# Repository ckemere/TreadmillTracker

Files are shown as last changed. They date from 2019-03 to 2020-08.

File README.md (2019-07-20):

# Raspberry pi based interface for a rodent treadmill

  - MSP430 based HW data acquisition "hat"
  - Rotational angle tracking using the CUI AMT 102/3 quadrature encoders
  - 1 kHz master clock for timestamping 8 IO lines

## Setup overview

### PiHat
The custom Raspberry Pi hat contains several useful features.
- **Eight GPIO pins** can be used for either receiving or sending signals.
- **Encoder data (AMT102)** is received through the six pins at the top of the board.  
- **2 kHz master clock (DSC6083)** reliably timestamps input data.
- **Button** ?
- **MSP430 microcontroller** packages and sends serial messages containing timestamped data every 2 ms. Programmed via seven pins at bottom of board.
- **Shield** interfaces with Raspberry Pi pins, including the eight GPIO pins connected to RaspPi GPIO pins.

### Accessories
#### Rotary encoder
The AMT102 sends signals in increments with resolution of 4096 steps/revolution. Thus each pulse signals that the wheel has turned 1/4096 of a revolution. For more details, look at the specs in the data sheet contained in *Firmware*.

#### Lick sensor
The lick sensor sends digital signals to one of the Hat's GPIO pins to indicate a licking event is occurring. More details in lick-sensor repository.

#### Nose-poke sensor
The nose-poke sensor sends digital signals to one of the Hat's GPIO pins to indicate a nose-poke event is occurring.

#### Syringe pump
The syringe pump receives 5V pulses from a GPIO pin on the Hat to dispense liquid rewards. The duration of the pulse determines the volume of reward dispensed (given a syringe diameter and pump speed).

#### Sound card
The sound card converts the digital audio file (.wav) to an analog signal to drive the external speakers. It can either be integrated with the host computer (if using a desktop), or as a shield (if using a Raspberry Pi; the HiFiBerry Amp2, for example, uses built-in drivers in the Raspberry Pi Linux kernel to obtain high-quality I2C digital audio from the GPIO pins, which it converts to an analog signal for speaker input. See [here](https://www.hifiberry.com/build/documentation/configuring-linux-3-18-x/) for more details.)

#### Breakout board
In order to streamline I/O connections between the custom hat and accessories, a custom breakout board shield connects GPIO pins to the rings of 3.5 mm audio jacks. Additionally, the hat Vdd (3.6 V) can be routed to supply voltage to the tips of the audio jacks. With this setup, audio cables can transmit GPIO signal to input and from output devices listed above. For example, audio cables can carry lick and nose-poke sensor digital signals, or send dispense signals to the syringe pumps.

### Host computer
The host computer can either be a Raspberry Pi or a desktop computer. If using a Raspberry Pi, then the custom hat and sound card shield can be stacked on top of one another to form a three-layer, stand-alone device. Otherwise, the host computer is connected to the custom hat via USB, and the native desktop sound card is used to drive the external speakers. In either case, the following components must be installed on the computer.

#### Mixer
The combination of the JACK Audio Connection Kit and minimixer allows for cross-talk between audio sources to function as a software mixer for different audio signals. The JACK daemon runs in the background as a sound server, built on top of the Advanced Linux Sound Architecture (ALSA), for a particular output device (sound card). In a separate process, the minimixer receives different audio feeds in its virtual channels, and controls each sound level of each channel that it feeds into the JACK daemon based on OSC commands it receives. Thus the user has control to dynamically change the output levels of different virtual channels in the minimixer.

#### OSC interface
The mixer, in turn, is interfaced through an OSC package, such `oscpy` in Python, that binds and sends OSC commands to the same port as the mixer. The commands direct the mixer to increase or decrease the gain for each channel in the mixer.

#### Control script
The control script must manage I/O from all the above components, including:
- Processing **behavior input** from the custom hat to determine the current behavior state. The input messages via the serial interface include current time, wheel encoder position, and GPIO values.
- Controlling **audio output** by launching appropriate audio subprocesses (e.g. daemon, mixer) and sending OSC commands to the mixer based on the current behavior state.
- Controlling **behavior output** by sending dispense pulses to the GPIOs associated with syringe pumps based on the current behavior state.

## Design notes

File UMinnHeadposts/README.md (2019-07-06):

This is a design adapted from that developed by Ghanbari et al and presented in the paper
["Cortex-wide neural interfacing via transparent polymer
skulls"](https://www.nature.com/articles/s41467-019-09488-0) from the lab of Suhasa
Kodandaramaiah at the University of Minnesota. Various curves have been replaced with simpler
splines, mounting holes stretched to 5.5mm, and the 3D printed base and metal frames have been
made to be symmetrical (the 3D printed base at least has a symmetrical hole).

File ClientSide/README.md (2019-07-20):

# Notes on using the Treadmill Tracker

### Using the direct USB interface

#### Set up
Install the udev file in /etc/udev/rules.d directory. This file sets up the proper permissions
for the FT230X interface as well as the latency (see below). Also, add yourself to the proper
groups.

```
sudo cp 60-ftdi-latency.rules /etc/udev/rules.d/
sudo usermod -a -G tty <your-username>
sudo usermod -a -G dialout <your-username>
```

#### Expectations
We are sending 9 byte messages at 256000 baud. Since there is an extra stop byte per serial
transaction, our messages are actually 9 x 9 or 81 bits long, and so our sustained rate can at
most be 256000/81, or more interestingly, our minimum transaction period can be 81/256000 or
0.31 ms. Given that the USB transaction rate is expected to have a period of at least 1 ms, we
suspect the best we can do is 2 ms data transmission rates.

#### Quantifying latency
There's several ways of quantifying latency. 

##### Message rate latency
Since in the absence of any triggered outputs we know the rate that the MSP430 is sending data,
for this project we can also ask what the time difference between receipt of serial packets is.
`TestInterEventInterval.py` records the time of each packet to a data file. When we do this
with a naive Ubuntu 18.04 installation, we find that we can't get packets more than about every
15 ms. Given that the USB 2.0 interval should be 0.125 ms or somesuch, this is disappointing.
Reading through the driver source
(https://git.kernel.org/pub/scm/linux/kernel/git/torvalds/linux.git/tree/drivers/usb/serial/ftdi_sio.c),
we find reference to a "latency timer". Reading up on that, it appears that this is what
controls how often the FTDI chip sends data (either whenever its 512 byte buffer is full *or*
when the latency timer expires). More reading tells us that we can find the current value of
the latency timer by looking in /sys/bus/usb-serial/devices/ttyUSB0/latency_timer (or whatever
the proper ttyUSB is). Reading this file, we find the value "16"!? If we try to write to this
file, it gives an error message (even with superuser). A little more searching, and we find a
comment on a [blog post](https://projectgus.com/2011/10/notes-on-ftdi-latency-with-arduino/)
that points out we can make a UDEV rule. So, finally, we edit the file
`/etc/udev/rules.d/60-ftdi-latency.rules`:

```
# Lower the latency timer for the FTDI serial interface
ACTION=="add", SUBSYSTEM=="usb-serial", DRIVER=="ftdi_sio", ATTR{latency_timer}="1"
```

Now, setting the transmit rate to 5 ms, we find a median rate of 5 ms, with a max of 6.3 ms
measured over 27K messages! With a transmit rate of 2 ms, we find a median rate of 2 ms, with a
max of 3.2 over 50K messages.

For Windows, we find instructions on how to set the latency timer here: [https://www.ftdichip.com/Support/Knowledgebase/index.html?settingacustomdefaultlaten.htm](https://www.ftdichip.com/Support/Knowledgebase/index.html?settingacustomdefaultlaten.htm). In summary, open the registry editor (`regedit`) and navigate to the key:
`HKEY_LOCAL_MACHINE\SYSTEM\CurrentControlSet\Enum\FTDIBUS\{Device VID, PID and serial number}\0000\Device Parameters\LatencyTimer`
Then change its value to `1`.

An interesting and open question is how to set the latency timer for OSX.

##### Closed loop latency
Another way of measuring latency is to ask how fast we can see a change that we trigger.
`TestClosedLoop.py` uses the reported time stamps to do this. The basic idea is to wait until a
particular timestamp is received, trigger an output, and then see what the timestamp is for the
trigger-based message comes back. When the latency timer was large, this gave interesting
results. Now, it mainly reports 1 ms results, which aren't particularly interesting.

### Using the Raspberry Pi interface
The shield does not work out of the box (with a Ubuntu server image, e.g., ubuntu-19.04-preinstalled-server-armhf+raspi3.img.xz from here:[http://cdimage.ubuntu.com/releases/19.04/release/]). We need
to mess with boot settings. General notes about the Raspberry Pi HW serial ports
are [here](https://www.raspberrypi.org/documentation/configuration/uart.md). The
upshot is that we need to do two things. 

  - First, swap the bluetooth interface to the secondary MiniUART by adding a
    line to `/boot/firmware/config.txt`, `dtoverlay=pi3-miniuart-bt`. (Note that
    `dtoverlay=pi3-miniuart-bt` worked, but `pi3-disable-bt` didn't for some reason!)
  - Second, we need to remove the debug console from the serial port, by
    deleting the `console=serial0,115200` and `console=tty1` commands from
    `/boot/firmware/cmdline.txt`.

Then, when the shield is plugged into the Raspberry pi, the serial device is
`/dev/ttyAMA0`, which is different from the default for the FT230 driver, which
is `/dev/ttyUSB0`!

To control GPIO with the Raspberry Pi, there are a number of libraries. Our favorite,
`pigpio` is not yet working with a 64-bit kernel. The new kernel library for IO
is `libgpiod`. Hopefully we'll eventually switch to that interface. For now,
we're using RPi.GPIO, which is a fairly standard Raspberry PI Python GPIO
library. RPi.GPIO is also sensitive to architecture. See
[here](https://alioth-lists.debian.net/pipermail/pkg-raspi-maintainers/Week-of-Mon-20190318/000333.html)
for a description of what needs to be done to get it to work. Basically two
things: (1) making sure that the CPU detection code doesn't rely on
`/proc/cpuinfo` (this is already patched in RPi.GPIO, but a recent version needs
to be used) and (2) making sure that `/dev/mem` can be accessed. As described in
the link above, 
> So, it fails to open `/dev/mem`. That's because the Debian kernel is
> built with `CONFIG_DEVMEM_STRICT=y`. To work around that, we need to add
> `iomem=relaxed` to the kernel command line in `/boot/firmware/cmdline.txt`

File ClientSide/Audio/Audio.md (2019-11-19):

## Basic Plan: JACK audio with a mixer controlled by OSC commands

This has been tested on an updated Ubuntu 18.04 installation on the desktop and on a Ubuntu 19.04 server installation on the Raspberry Pi (i.e., ubuntu-19.04-preinstalled-server-armhf+raspi3.img.xz from here:[http://cdimage.ubuntu.com/releases/19.04/release/]).

### Testing

***Remember:*** If stuff is weird on the laptop it may be because anaconda has
stolen our path!!!

#### Install jack
Install the jack daemon and tools. In order to get realtime priority, you'll also need
to be a member of the audio group. (*You'll likely need to reboot for the group addition
to take effect.*)

```
sudo apt install libjack-jackd2-dev jack-tools
sudo usermod -a -G audio <your-username>
```

### (optional) Install ubuntu studio control
ubuntustudio-controls ubuntustudio-performance-tweaks

#### jackminimix
[https://github.com/njh/jackminimix/]

```
# Install required packages
sudo apt install liblo-tools liblo-dev autotools-dev autoconf automake

# Install jackminimix
git clone https://github.com/njh/jackminimix.git
cd jackminimix
./autogen.sh
./configure
make
make install
```

Note that there's a 'GAIN_FADE_RATE` value which is defined as 400 db/minute.
This gives nice transitions, but extends sounds a bit.

#### jackmeter
Useful to see stuff working

#### sndfile-jackplay
[https://github.com/erikd/sndfile-tools/]

```
# Install required packages
sudo apt install libtool libsndfile1-dev libsamplerate0-dev libfftw3-dev libcairo2-dev

# Install sndfile-tools
git clone https://github.com/erikd/sndfile-tools.git
cd sndfile-tools
./autogen.sh
./configure
make
sudo make install
```

#### GPIO

To install the newest and greatest RPi.GPIO, we have to `pip` from the source
repository. Since it's hosted in SVN, we need to `apt install mercurial`. Then,
we can `pip3 install hg+http://hg.code.sf.net/p/raspberry-gpio-python/code#egg=RPi.GPIO`
This solves issues with `/proc/cpuinfo`, but still raises a `Cannot access
/dev/mem` error unless run with root, and even then you need a fancy thing in
the `cmdline.txt` file. See [README.md].

#### How do we test

  - Use `mplayer -ao jack Linchirp.ogg -loop 0` to loop audio files (plays wav also).
  - Start up JackMiniMixer. Start as `./jackminimix -v` (verbose option is useful for feedback.)
  - Use qjackctl to make sure that everything gets connected (i.e., different audio sources to
    different mixer channels) graphically. There probably is a command line way too?
  - Send OSC commands to control stuff. E.g., `oscsend "osc.udp://localhost:14161" "/mixer/channel/set_gain" if 2 -10.0`
  - *NOTE* If you don't hear anything or it's too loud, check alsamixer for volume with JACK
    running

  - We've added a gapless looping wave file player from the sndfile-tools
    library. For some reason the packaged version doesn't connect to the jack
    daemon, but we've copied the source into the PlaySound directory. Compile
    with ' '
  - To play, use `./PlaySound/jplay -l0 -a=minimixer:in1_right 15khz_sine.wav`.
    Note that the `-l 0` flag loops infinitely (gapless FTW!) and the `-a` flag
    specifies to send data to the minimixer. Can just skip that to test.
    Other stuff is here -
    [http://mega-nerd.com/libsndfile/tools/](http://mega-nerd.com/libsndfile/tools/).

  - `jack_lsp --connections` is a useful command for seeing what the connections are.

  - The $1M question is what is the latency from detecting an event (i.e., a
    nose poke) to modulating the sound. To test this, we need to run the JACK
    daemon, the minixer, and a Python script which sends osc commands based on
    IO.
       1. Start JACK: `jackd -R -P10 -v -d alsa -p64 -n2 -P hw:1,0` (`-R` is
          realtime, `-P` priority is 10, -v verbose, `-d` set alsa output device,
          `-p 64` set the buffer to be small and `-n 2` have a minimal number of
          buffers, and `-P hw:1,0` set the proper soundcard) We could also add
          a `-r 192000` to set the sampling rate. Check for the proper soundcard by listing audio devices with `aplay -l`, and looking for the numbers associated with the desired sound card and device on it. (`hw:<#>,<#>` stands for *hardware: card_number, device_number*.) See [here](https://www.mankier.com/1/jackd) for a nice list of available command-line parameters (including backends).

       2. Start the minimixer: `jackminimix -a -p 12345` (optionally `-v` to
	  see commands coming through.) Note that `12345` is the port for osc
          control. You can change it to something else, but make sure your other
          code matches. If you need to swap the input/output connections, run `jackminimix -l <input_ID> -r <input_ID> -p 12345`, where `<input_ID>` is the input to the left and right outputs of the mixer, respectively. (e.g. `system:playback_1`).

       3. Start an audio loop playing into the mixer: `./PlaySound/jplay -l0
          -a=minimixer:in1_right 15khz_sine.wav`

       4. Figure out what the minimix port is, and then set it and run the test
          script `sudo python3 TestPiAudioControl.py`. It has to be run as root
          because RPi.GPIO appears to require it. This script toggles pin 17
          every 200 ms, while continuously reading from the UART data stream. If
          it detects a changed value on pin 16, it sends an OSC message to
          either make the gain 0.0 dB (full volume) or -30.0 dB. Putting the
          oscilloscope on pin 16 and the speaker, we see sound changes starting
          about 6-7 ms following the edge of the pin. This is consistent with
          first a worst-case UART sampling delay of 2 ms  followed by a few
          sound buffers worth of latency. (Note that with `-p64`, each buffer is
          *1.3 ms* long, so with `n2`, that means a minimum of 2.6 ms of
          latency. I guess the minimixer 

#### Running audio in background
Optional arguments can vary. See above for details.

```
# Start jack daemon
jackd --realtime -P 10 -d alsa -p 128 -n 2 -r 96000 -P hw:0,0

# Start jackminimix on port 12345
jackminimix -a -p 12345

# Play sounds in different channels continuously
sndfile-jackplay -l0 -a=minimixer:in1_right pink_noise.wav
sndfile-jackplay -l0 -a=minimixer:in2_right tone_cloud.wav
sndfile-jackplay -l0 -a=minimixer:in3_right tone.wav
```

#### Some notes on JACK
JACK creates virtual connections between audio sources and targets, typically for one device (e.g. sound card). We can specify which device JACK manages by adding the `-d` or `-P` flag *after* the `alsa` flag:

```
jackd --realtime -P 10 -d alsa -p 128 -n 2 -r 96000 -d hw:0,0
```

See notes above for determining the device name (one could also use the shorthand name found from the commmand `cat /proc/asound/cards` in the format `hw:<name>`; see [here](https://jackaudio.org/faq/device_naming.html) or [here](https://superuser.com/a/53977) for more details.). Once the device is found, JACK will then automatically create the appropriate virtual input and output ports that correspond to those on the device. For example, when specifying a Xonar DG sound card in the command above, JACK creates six output ports, one for each native output port in the sound card: front left, front right, side surround, center surround/subwoofer, S/PDIF digital output, and front panel. We can view this by opening the GUI QjackCtl (by simplying running `qjackctl` from the command line):

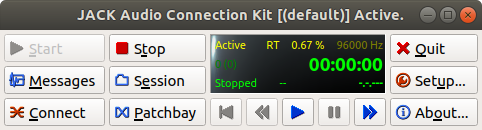
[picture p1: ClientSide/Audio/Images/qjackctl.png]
QjackCtl


and clicking the "Connect" button on the bottom left.

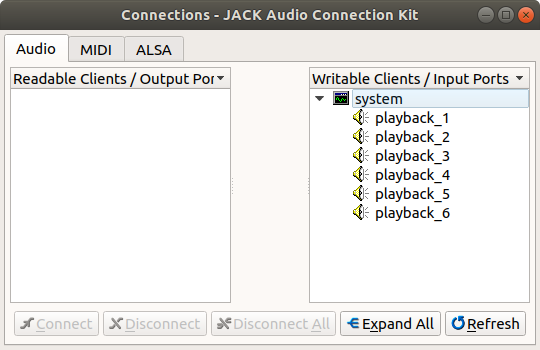
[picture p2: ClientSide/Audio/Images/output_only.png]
JACK output ports


As we can see, JACK has already recognized the six output ports on our Xonar DG sound card, and named them accordingly: `system:playback_x`, which is the default name for raw MIDI ports on the ALSA driver (as implemented [here](https://github.com/jackaudio/jack2/blob/master/linux/alsarawmidi/JackALSARawMidiPort.cpp#L48); likewise, input ports are assigned the names `system:capture_x` by default). Next, we fire up the minimixer from the command line, using the `-a` flag for auto-connection and allowing the default of four input channels (which can be specified with the `-c` flag): 

```
jackminimix -a -p 12345
```

and view the updated connections on QjackCtl:

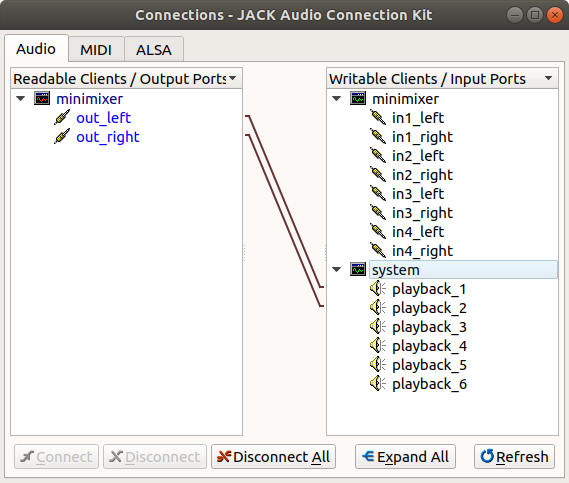
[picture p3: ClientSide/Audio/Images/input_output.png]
Minimix and Jack


Because the JACK minimix is "JACK aware", it detected the running JACK server and automatically connected its output ports to the first two playback ports on the server. These correspond to "front left" and "front right" on our sound card. Note the minimix can set up any number of input channels (within limits), each of which contain a left and right side, but only one output channel with left and right sides; the actual output is determined by the sum of the inputs plus the MIDI commands for each input channel that determine its gain. We could achieve the same goal by specifying to which JACK playback ports the left and right minimix outputs connect:

```
jackminimix -l system:playback_1 -r system:playback_2 -p 12345
```

Finally, let's discuss how we route the sound to multiple outputs. We have two options:
1. Create a stereo audio file with the desired number of outputs. Play the sound using `sndfile-jackplay` without specifying any ports (i.e. do not use the `-a` flag). This will route the stereo file appropriately so that the channels in the stereo file will align with the corresponding outputs. Make sure that the ALSA driver has Analog Output set to Stereo mode by using the `alsamixer` command.
2. Feed mono audio files into the left or right channels of the minimixer using the flag `-a=minimixer:in<channel>_<side>`, where `channel` is the channel number and `side` is left or right. (If you get confused, simply refer to the writeable ports listed in QjackCtl.) The volume of each channel (but not left or right side individually) can be controlled by sending `osc` commands to the minimixer as detailed above. Unlike the first method, this method is limited the just two outputs (left and right). Make sure that the ALSA driver has Analog Output set to Multichannel mode. Also, check that the speaker balance is set appropriately so that one side isn't muted!

### OSC commands

#### Python

  - Wrote a Python script to make a pure tone sinewave at arbitrary sampling
    rates - `GenerateTone.py`. Note that the gain was weird when we tried to
    write it as a mono file instead of stereo.

  - Python script that sends OSC commands uses `oscpy` library. `pip3 install
    oscpy` gets it.

#### Command line

example `oscsend "osc.udp://localhost:12345" "/mixer/channel/set_gain" if 2 -10.0`

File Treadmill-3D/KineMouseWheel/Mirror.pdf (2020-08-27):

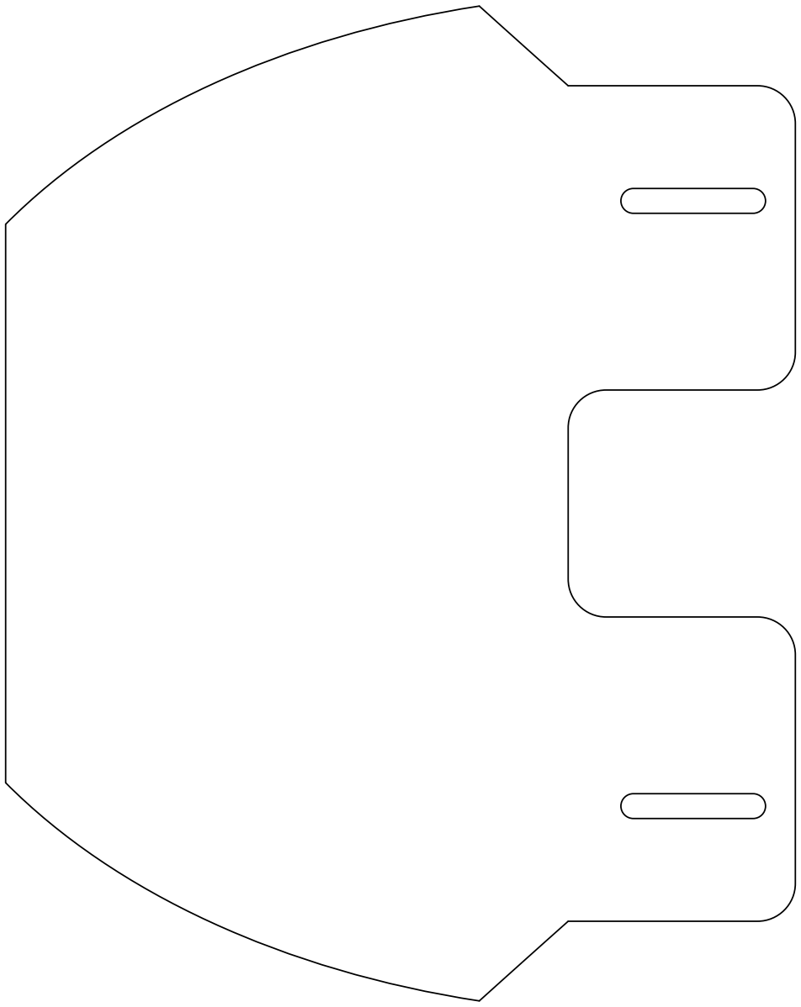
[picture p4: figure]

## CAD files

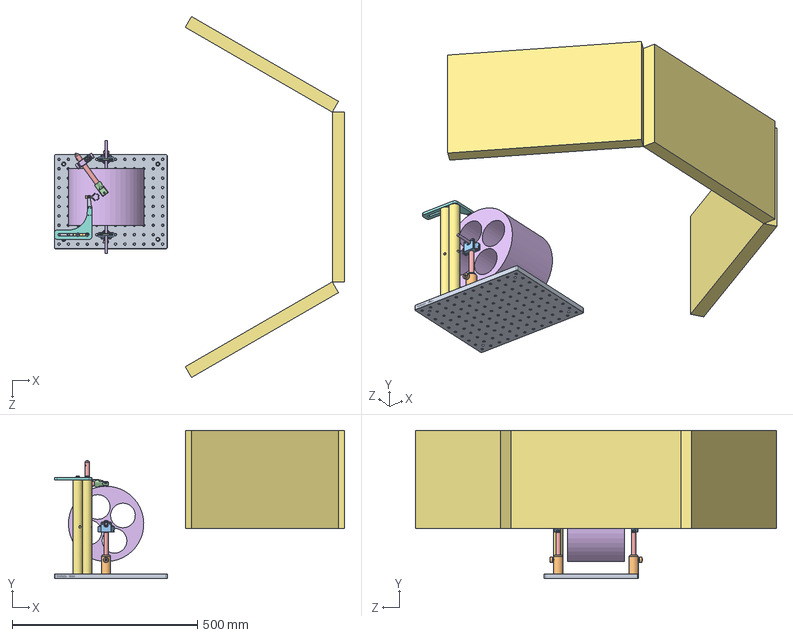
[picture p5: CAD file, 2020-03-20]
Treadmill-3D/SingleWheel/OtherParts/Head Fixed Assembly 20in.SLDASM
783.1 x 400.2 x 973.5 mm
MB1012-Solidworks
PH2-Solidworks x 2
BearingAdaptor-SensorMount-PostMount-Centered x 2
8600N300_LOW-PROFILE MOUNTED BALL BRNG W ALUM HOUSING x 2
TR4-Solidworks x 3
Wheel
RS10 x 2
SideRearHeadPlateArm
SideHeadPlateHolder
Headplate
SH25LP38-Solidworks x 2
LickSpoutHolder
TR12-Solidworks
RA90-Solidworks
20 in monitor x 3

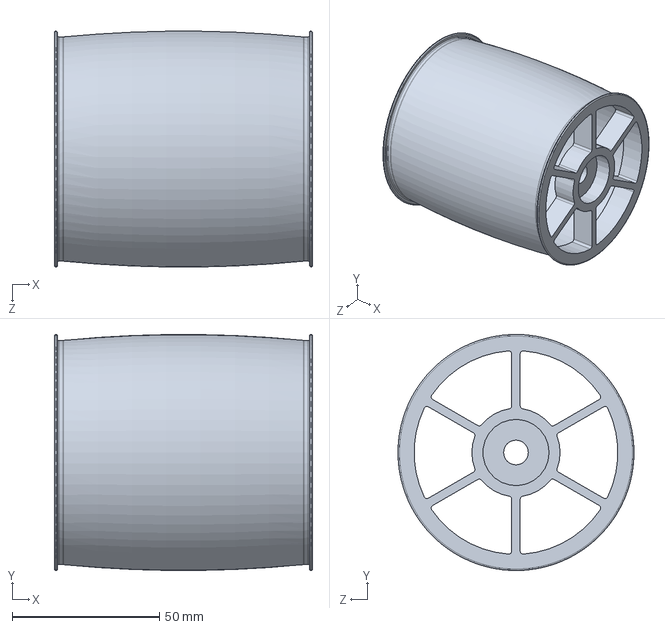
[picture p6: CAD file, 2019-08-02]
Treadmill-3D/FullTreadmill/Pulley_3_5in_Full_bearing.SLDPRT
87.6 x 80.2 x 80.2 mm

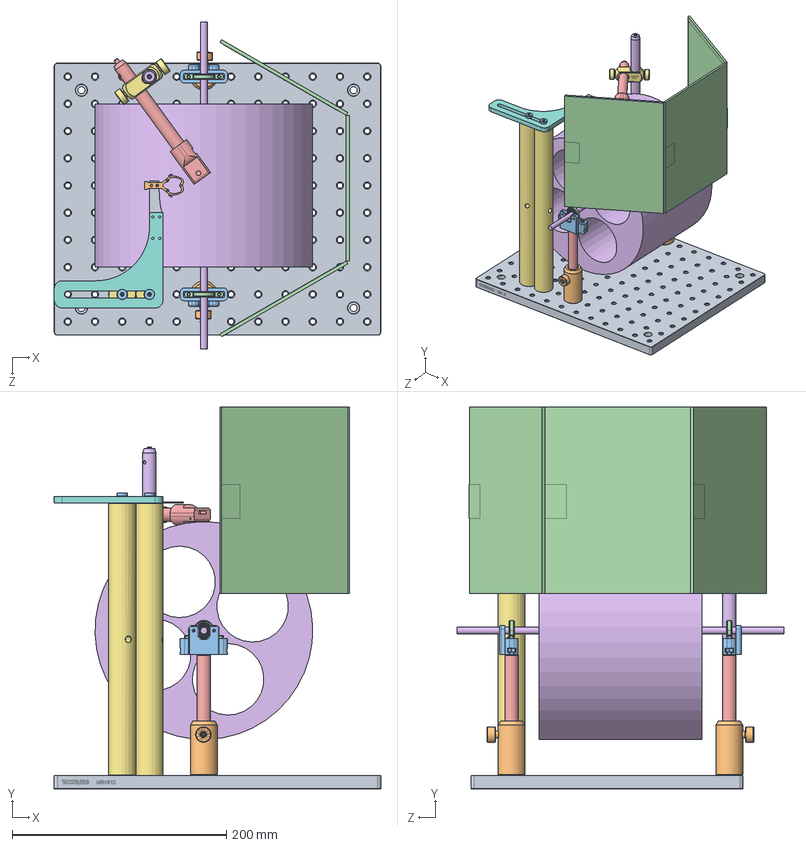
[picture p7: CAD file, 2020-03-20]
Treadmill-3D/SingleWheel/OtherParts/Head Fixed Assembly.SLDASM
304.8 x 356.5 x 304.8 mm
MB1012-Solidworks
PH2-Solidworks x 2
BearingAdaptor-SensorMount-PostMount-Centered x 2
8600N300_LOW-PROFILE MOUNTED BALL BRNG W ALUM HOUSING x 2
TR4-Solidworks x 3
Wheel
RS10 x 2
SideRearHeadPlateArm
SideHeadPlateHolder
Headplate
SH25LP38-Solidworks x 2
Single 8in Screen x 3
LickSpoutHolder
TR12-Solidworks
RA90-Solidworks

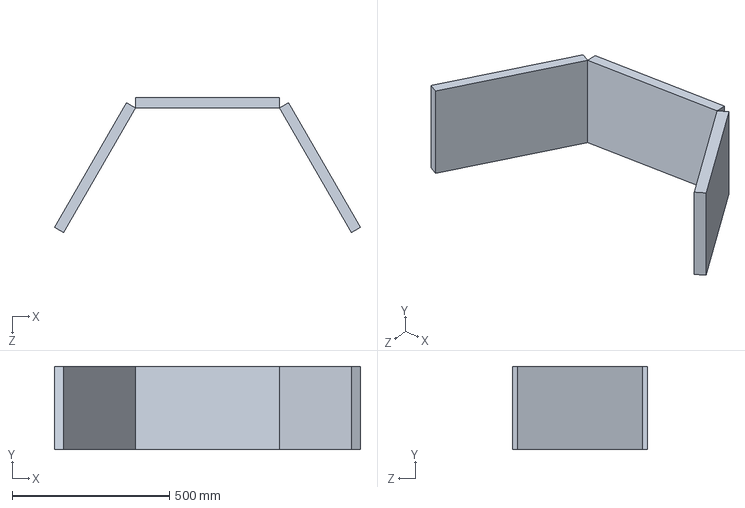
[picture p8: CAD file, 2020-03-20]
Treadmill-3D/SingleWheel/VR/ThreeScreenAssembly.SLDASM
973.5 x 264.9 x 429.9 mm
20 in monitor x 3

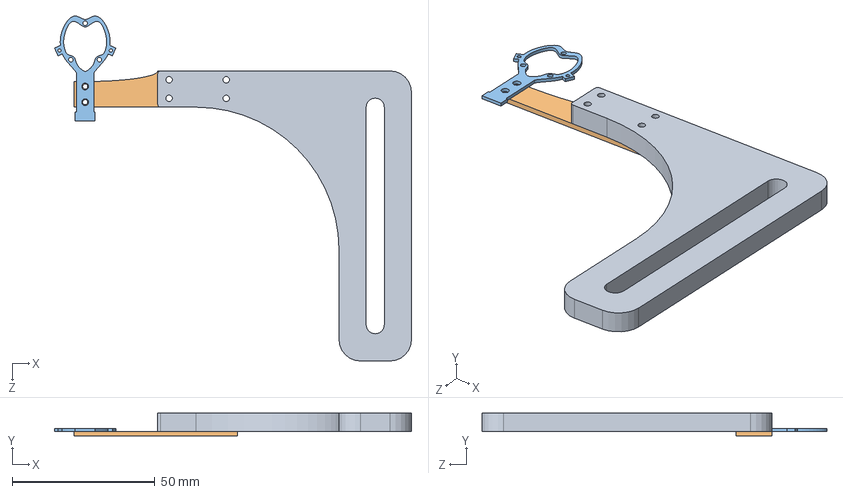
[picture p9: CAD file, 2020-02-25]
UMinnHeadposts/Head Post Holder Asembly.SLDASM
125.1 x 7.94 x 120.8 mm
SideRearHeadPlateArm
SideHeadPlateHolder
Headplate

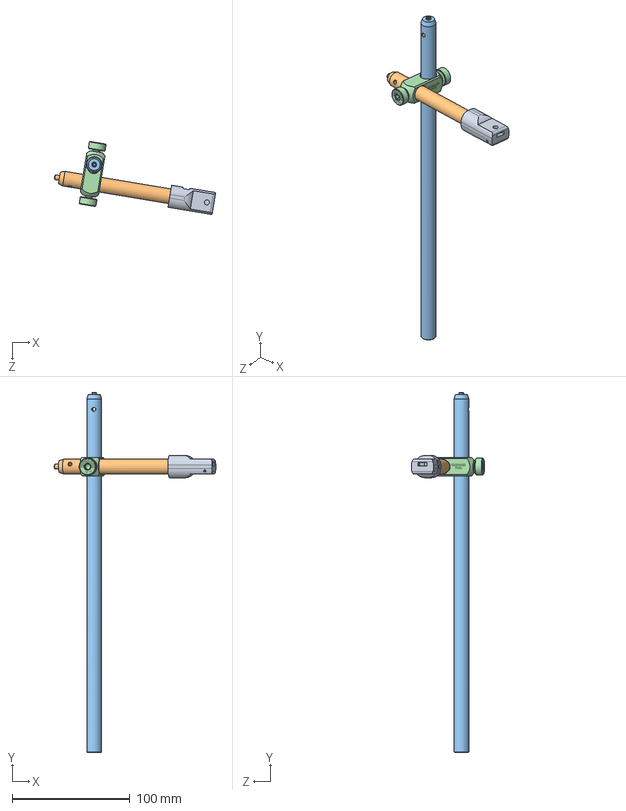
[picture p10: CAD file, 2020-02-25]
Treadmill-3D/SingleWheel/OtherParts/Reward Tube Assembly.SLDASM
137.5 x 306.4 x 62.3 mm
LickSpoutHolder
TR4-Solidworks
TR12-Solidworks
RA90-Solidworks

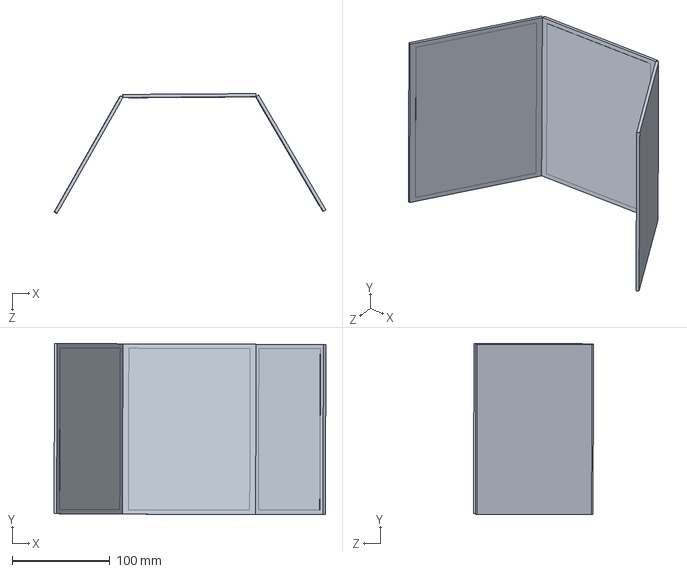
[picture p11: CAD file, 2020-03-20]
Treadmill-3D/SingleWheel/VR/Screen Assembly.SLDASM
277.8 x 175.0 x 122.4 mm
Single 8in Screen x 3

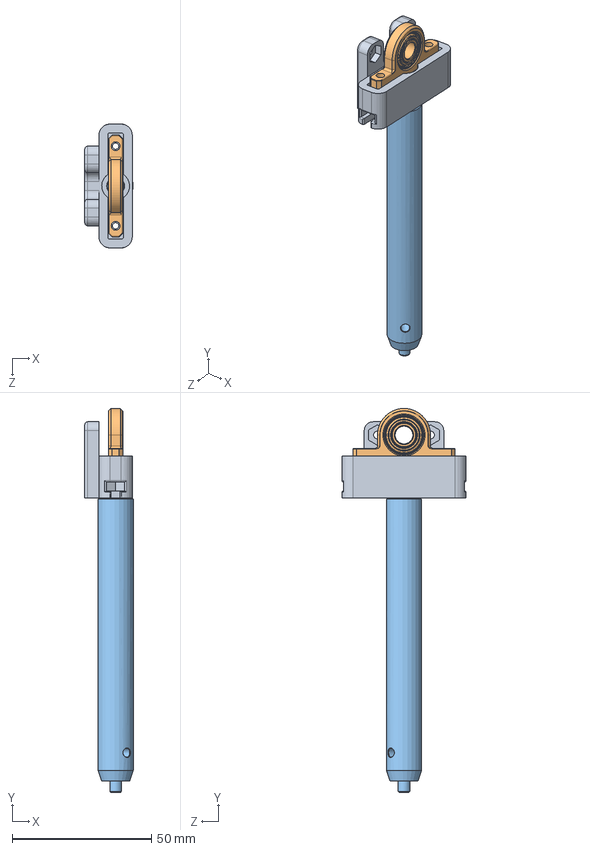
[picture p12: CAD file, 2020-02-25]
Treadmill-3D/SingleWheel/OtherParts/Bearing Post Assembly.SLDASM
17.4 x 137.8 x 44.5 mm
BearingAdaptor-SensorMount-PostMount-Centered
8600N300_LOW-PROFILE MOUNTED BALL BRNG W ALUM HOUSING
TR4-Solidworks

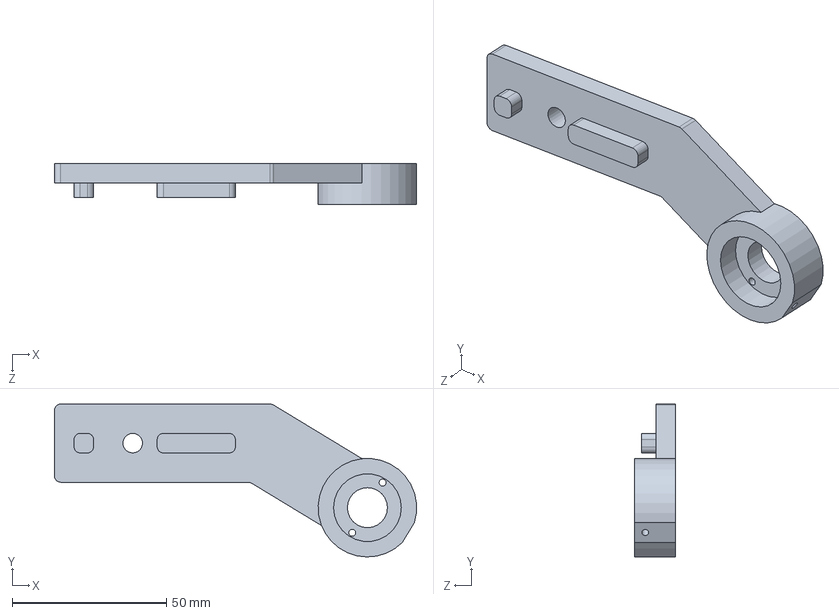
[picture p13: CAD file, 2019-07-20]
Treadmill-3D/FullTreadmill/3D Printed/BearingMountWithEncoder.SLDPRT
117.5 x 49.6 x 13.3 mm

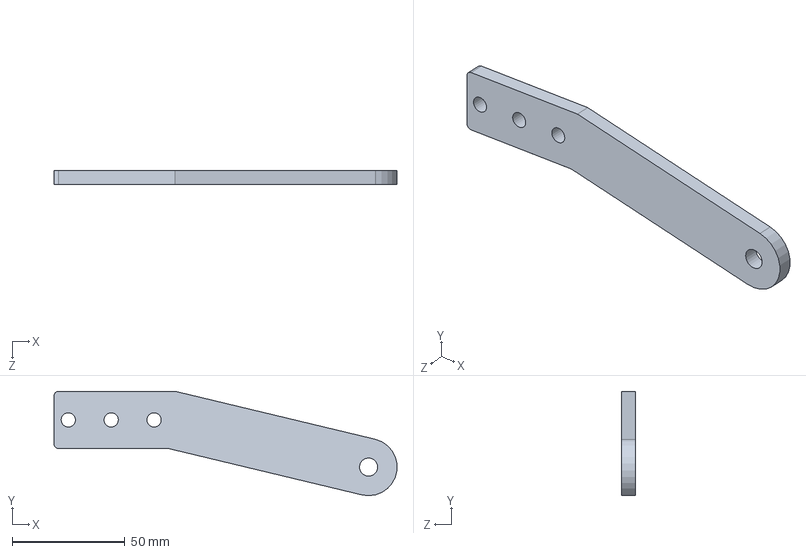
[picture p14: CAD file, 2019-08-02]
Treadmill-3D/FullTreadmill/Laser Cut/Axel Mount Long.SLDPRT
152.3 x 46.3 x 6.35 mm

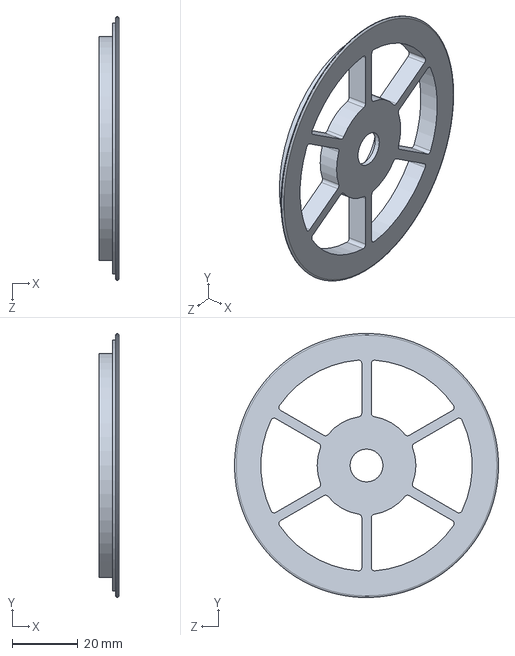
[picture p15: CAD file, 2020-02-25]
Treadmill-3D/FullTreadmill/Pulley_3_5in_EndCap-Bearing.SLDPRT
6.00 x 80.2 x 80.2 mm

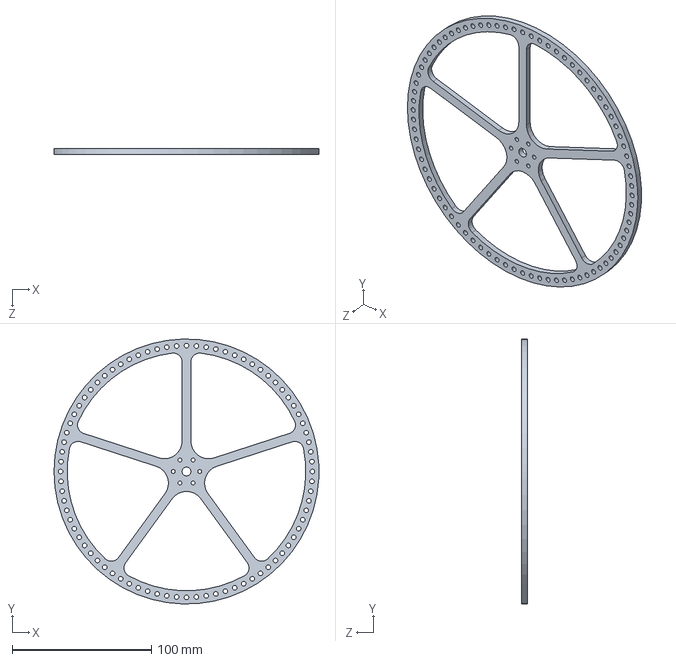
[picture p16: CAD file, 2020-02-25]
Treadmill-3D/KineMouseWheel/Spokes.SLDPRT
190.5 x 190.4 x 4.00 mm

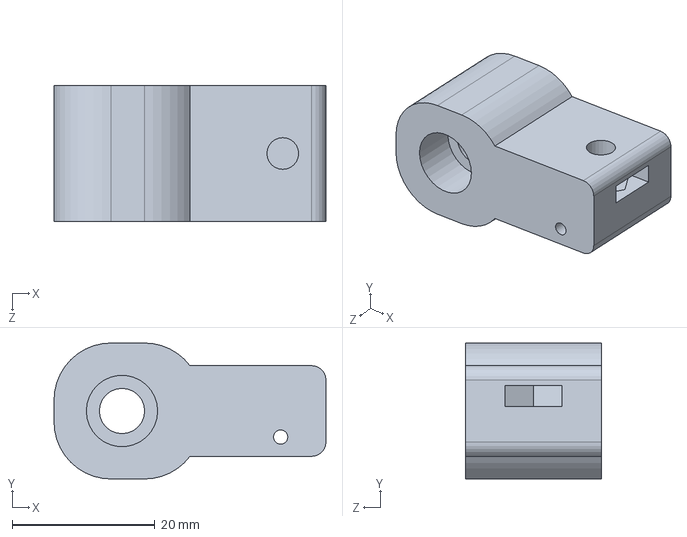
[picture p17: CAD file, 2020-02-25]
Treadmill-3D/Lick Spout Holder Inline Post.SLDPRT
38.1 x 19.1 x 19.1 mm

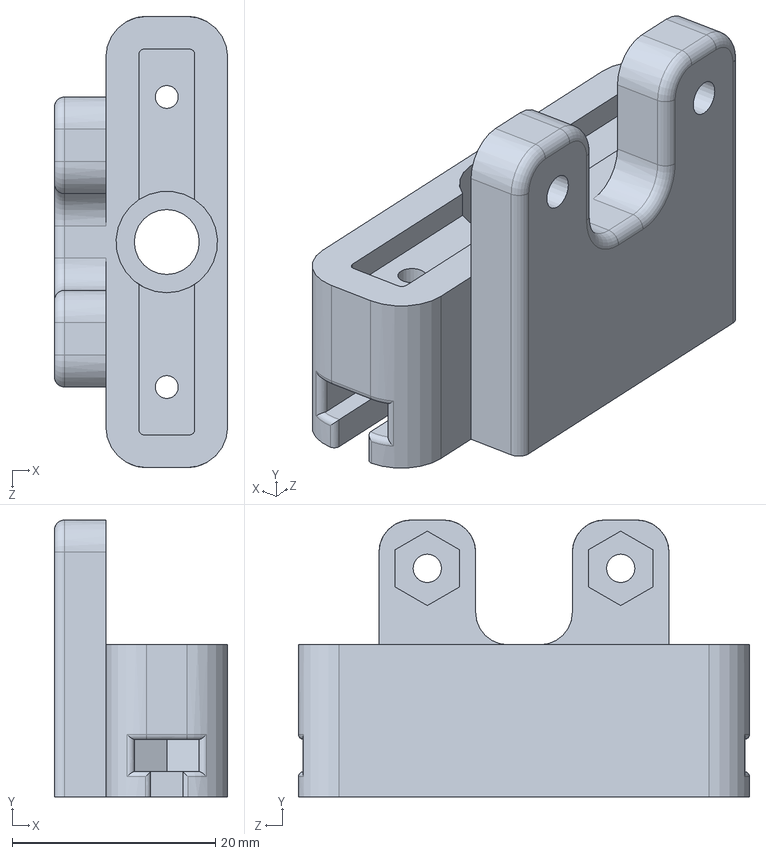
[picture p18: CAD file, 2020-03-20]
Treadmill-3D/SingleWheel/BearingAdaptor-SensorMount-PostMount-Centered.SLDPRT
17.1 x 27.3 x 44.5 mm

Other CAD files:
Treadmill-3D/SingleWheel/VR/Single 8 in Screen and Controller Board Holder.SLDPRT
UMinnHeadposts/SideHeadPlateHolder 4_72 mm.SLDPRT
Treadmill-3D/3DPrintedWheel.SLDPRT
Treadmill-3D/FullTreadmill/3D Printed/BearingMount - Right.SLDPRT
Treadmill-3D/3 inch spacer.SLDPRT
Treadmill-3D/3 inch spacer.STL
Treadmill-3D/AxelAdaptor.SLDPRT
Treadmill-3D/AxelAdaptor.STL
Treadmill-3D/AxelAdaptor1375.SLDPRT
Treadmill-3D/AxelAdaptor1375.STL
Treadmill-3D/AxelSpacer_2310.SLDPRT
Treadmill-3D/AxelSpacer_2310.STL
Treadmill-3D/BearingMount-80-20.SLDPRT
Treadmill-3D/BearingMount-80-20.STL
Treadmill-3D/BearingMountSlider.DXF
Treadmill-3D/BearingMountSlider.SLDPRT
Treadmill-3D/BearingMountWithoutSlider.DXF
Treadmill-3D/BearingMountWithoutSlider.SLDPRT
Treadmill-3D/BearingMountWithoutSliderTightFit.SLDPRT
Treadmill-3D/BearingSliderTightFit.SLDPRT
Treadmill-3D/FullTreadmill/3D Printed/BearingMount - Right.STL
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

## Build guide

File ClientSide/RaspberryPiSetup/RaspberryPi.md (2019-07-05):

# Getting a Raspberry Pi up and running

These are installation instructions for use with the Ubuntu Server 19.04 pre-installed arm64 
images. They might work for other Ubuntu versions. They assume that you are running some sort
of Ubuntu variant on the desktop.

### 1. Getting the image
Download an official Ubuntu Server preinstalled image for the Raspberry Pi. For 19.04, this can
be found here: http://cdimage.ubuntu.com/releases/19.04/release/ The one you want is called 
`ubuntu-19.04-preinstalled-server-arm64+raspi3.img.xz`. This is the 64-bit version (Raspbian is
stuck at 32-bit at the moment), and designed for the Pi v3.

### 2. Writing it to disk
Put your SD card into your computer and figure out what device it is. In my case, when I run
GNOME Disks (which comes installed by default in 18.04), and I click on the SD Card, I see in
the title bar of the window `/dev/mmcblk0`. Further down in the window, I see `/dev/mmcblk0p1`,
but this is referring to the first partition, which is currently selected.

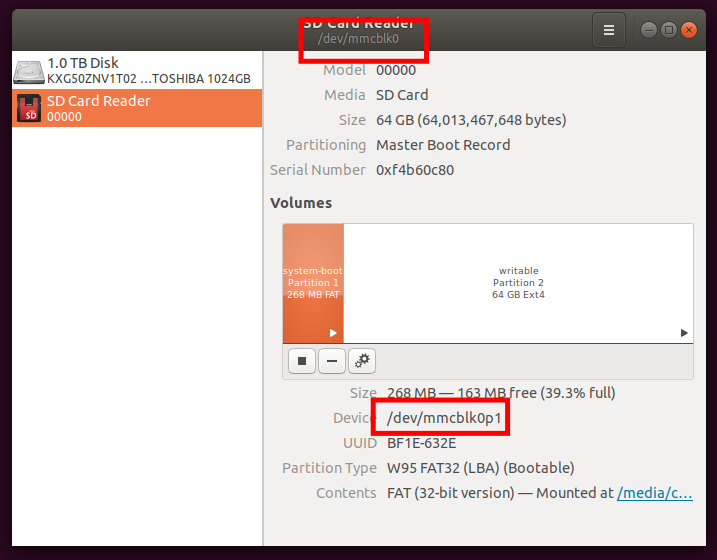
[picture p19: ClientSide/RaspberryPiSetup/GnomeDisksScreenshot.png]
Finding out device name


To write the image you've downloaded to the SD card, use the command: 
`xzcat ubuntu-19.04-preinstalled-server-arm64+raspi3.img.xz | sudo dd of=/dev/mmcblk0 bs=32M`.
What this does is uncompress the image and copy it bitwise to the device. This will end up
with a MBR and two partitions on the device.

### 3. Before you boot
Ubuntu Server now ships with cloud-init. If you follow their instructions for installation, it
will require you to have a working Ethernet connection upon first boot, and you'll end up with
a default user named `ubuntu`. I prefer to customize things a bit. Create two files,
`cloud.cfg` and `60-wifi.yaml`. Make the necessary changes in these files (edit the password
hash in `cloud.cfg` and the wifi password in `60-wifi.yaml`. These will set up a new user with
a pre-set password and the eduroam wifi. The text of the files are below. You should mount the
'writable' partitioni (not the boot one) of your just copied SD card, and copy these files into
place. In my setup, these get mounted at `/media/ckemere/writeable`. 

```
sudo cp cloud.cfg /media/YOURUSERNAME/writeable/etc/cloud/cloud.cfg
sudo cp 60-wifi.yaml /media/YOURUSERNAME/writeable/etc/netplan/60-wifi.yaml
```

### 4. Booting the Pi
Now, unmount the SD card (`umount /media/YOURUSERNAME/writeable` and `unmount
/media/YOURUSERNAME/system-boot` if you mounted the other partition) and remove it. Put it into
the Raspberry Pi, hook up an HDMI monitor, a keyboard, and a mouse, and plug in the
power. You'll see a bunch of stuff happening. The first boot takes a while, and the final
stages should complete with the generation of some SSH certificates. It took maybe 3-4
minutes for me.

After you get a login prompt, log in with the kemerelab account and the password you set up.
When you run `ifconfig` if the wireless worked ok, you should see an IP address assigned. Try
ssh'ing from another computer. You may need to reboot once before everything works.

### 5. Post first boot
Now you should be able to do other stuff. If you decide you want Ethernet, you can also copy
the Ethernet yaml file at the bottom of this page into the `/etc/netplan/`. Or perhaps you want
instead to read up on using static IP addresses and have a different netplan file.

If you successfully set up wireless, you should be able to access the internet and the package
repositories and install away. 

**Note:** Before I figured out all this, I was stuck trying to use Ethernet without a
connection outside of Rice. There are ways to tunnel apt through SSH. You can figure it out if
you Google/Bing enough...

#### `cloud.cfg`
This is almost the same as the default configuration, with just a couple of changes. Note that
the password hash is generated by `python3 -c 'import crypt,getpass;
print(crypt.crypt(getpass.getpass(), crypt.mksalt(crypt.METHOD_SHA512)))'`. I usually use the
lab default password, but put in a different one since this will be on github. You should
regenerate it for lab use with the default password!

```
# The top level settings are used as module
# and system configuration.

# A set of users which may be applied and/or used by various modules
# when a 'default' entry is found it will reference the 'default_user'
# from the distro configuration specified below
users:
   - default
################################################################################
   ##### Added for the kemerelab
   - name: kemerelab
     gecos: Kemerelab Default
     primary_group: kemerelab
     passwd: $6$ae.7mwNlox6iVCu/$5O8ZD3LzO.VYxOGjxuJLpSYEtfguVcVeqiGnLA0KMAenItT4.12d7.kdWxIu0zjq2PU8Dq3n2u8jfNItvjRxH/
     lock_passwd: false
     groups: [adm, audio, cdrom, dialout, dip, floppy, lxd, netdev, plugdev, sudo, video]
     sudo: ["ALL=(ALL) NOPASSWD:ALL"]
     shell: /bin/bash
################################################################################

# If this is set, 'root' will not be able to ssh in and they
# will get a message to login instead as the default $user
disable_root: true

# This will cause the set+update hostname module to not operate (if true)
preserve_hostname: false

################################################################################
##### Added for the kemerelab
network:
  config: disabled

ssh_pwauth: true
################################################################################

# Example datasource config
# datasource:
#    Ec2:
#      metadata_urls: [ 'blah.com' ]
#      timeout: 5 # (defaults to 50 seconds)
#      max_wait: 10 # (defaults to 120 seconds)

# The modules that run in the 'init' stage
cloud_init_modules:
 - migrator
 - seed_random
 - bootcmd
 - write-files
 - growpart
 - resizefs
 - disk_setup
 - mounts
 - set_hostname
 - update_hostname
 - update_etc_hosts
 - ca-certs
 - rsyslog
 - users-groups
 - ssh

# The modules that run in the 'config' stage
cloud_config_modules:
# Emit the cloud config ready event
# this can be used by upstart jobs for 'start on cloud-config'.
 - emit_upstart
 - snap
 - snap_config  # DEPRECATED- Drop in version 18.2
 - ssh-import-id
 - locale
 - set-passwords
 - grub-dpkg
 - apt-pipelining
 - apt-configure
 - ubuntu-advantage
 - ntp
 - timezone
 - disable-ec2-metadata
 - runcmd
 - byobu

# The modules that run in the 'final' stage
cloud_final_modules:
 - snappy  # DEPRECATED- Drop in version 18.2
 - package-update-upgrade-install
 - ssh-authkey-fingerprints
 - fan
 - landscape
 - lxd
 - ubuntu-drivers
 - puppet
 - chef
 - mcollective
 - salt-minion
 - rightscale_userdata
 - scripts-vendor
 - scripts-per-once
 - scripts-per-boot
 - scripts-per-instance
 - scripts-user
 - keys-to-console
 - phone-home
 - final-message
 - power-state-change

# System and/or distro specific settings
# (not accessible to handlers/transforms)
system_info:
   # This will affect which distro class gets used
   distro: ubuntu
   # Default user name + that default users groups (if added/used)
   default_user:
     name: ubuntu
     lock_passwd: True
     gecos: Ubuntu
     groups: [adm, audio, cdrom, dialout, dip, floppy, lxd, netdev, plugdev, sudo, video]
     sudo: ["ALL=(ALL) NOPASSWD:ALL"]
     shell: /bin/bash
   # Automatically discover the best ntp_client
   ntp_client: auto
   # Other config here will be given to the distro class and/or path classes
   paths:
      cloud_dir: /var/lib/cloud/
      templates_dir: /etc/cloud/templates/
      upstart_dir: /etc/init/
   package_mirrors:
     - arches: [i386, amd64]
       failsafe:
         primary: http://archive.ubuntu.com/ubuntu
         security: http://security.ubuntu.com/ubuntu
       search:
         primary:
           - http://%(ec2_region)s.ec2.archive.ubuntu.com/ubuntu/
           - http://%(availability_zone)s.clouds.archive.ubuntu.com/ubuntu/
           - http://%(region)s.clouds.archive.ubuntu.com/ubuntu/
         security: []
     - arches: [arm64, armel, armhf]
       failsafe:
         primary: http://ports.ubuntu.com/ubuntu-ports
         security: http://ports.ubuntu.com/ubuntu-ports
       search:
         primary:
           - http://%(ec2_region)s.ec2.ports.ubuntu.com/ubuntu-ports/
           - http://%(availability_zone)s.clouds.ports.ubuntu.com/ubuntu-ports/
           - http://%(region)s.clouds.ports.ubuntu.com/ubuntu-ports/
         security: []
     - arches: [default]
       failsafe:
         primary: http://ports.ubuntu.com/ubuntu-ports
         security: http://ports.ubuntu.com/ubuntu-ports
   ssh_svcname: ssh
```

#### `60-wifi.yaml`
Note that the indents are important in this file and must be spaces and not tabs.

```
network:
  version: 2
  wifis:
    wlan0:
      dhcp4: true
      dhcp6: true
      access-points:
        "eduroam":
          auth:
            key-management: eap
            method: ttls
            # anonymous-identity: ""
            identity: "ck19@rice.edu"
            password: "[ck19's password]"
        "YOUR HOME OR NON-ENTERPRISE HOTSPOT NAME":
          password: "YOUR HOME OR NON-ENTERPRISE HOTSPOT PASSWORD"

```

#### `50-ethernet.yaml`
Using the instructions above will bring up the system with only wifi enabled. If you also want
to use Ethernet, you need a second file in your /etc/netplan directory. The one below will set
up ethernet using dhcp. Note that for a standard Rice network port, this of course won't work
well, because while you'll be assigned an IP address, it requries authentication to actually
access the outside world. (Again, note that the indents are important in this file and must be
spaces and not tabs.)

```
network:
    version: 2
    ethernets:
        eth0:
            dhcp4: true
            optional: true
```

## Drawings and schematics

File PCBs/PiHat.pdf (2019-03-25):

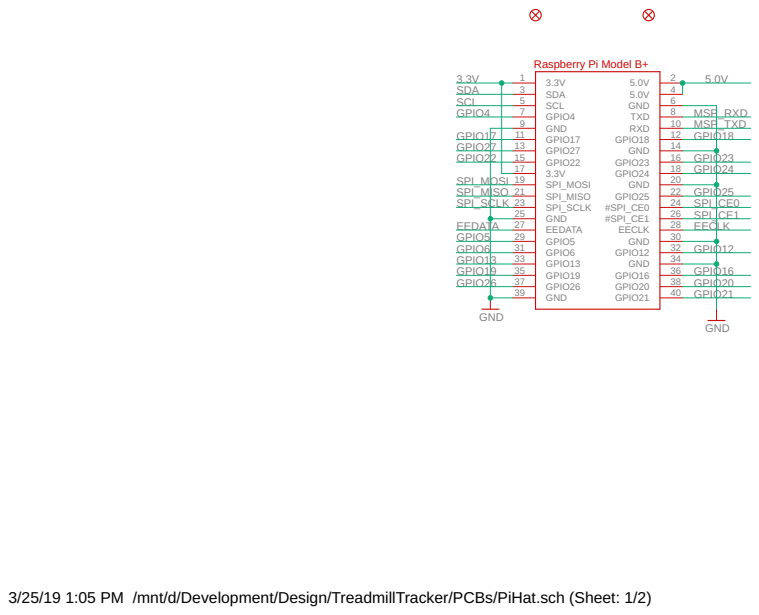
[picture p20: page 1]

3/25/19 1:05 PM /mnt/d/Development/Design/TreadmillTracker/PCBs/PiHat.sch (Sheet: 1/2)

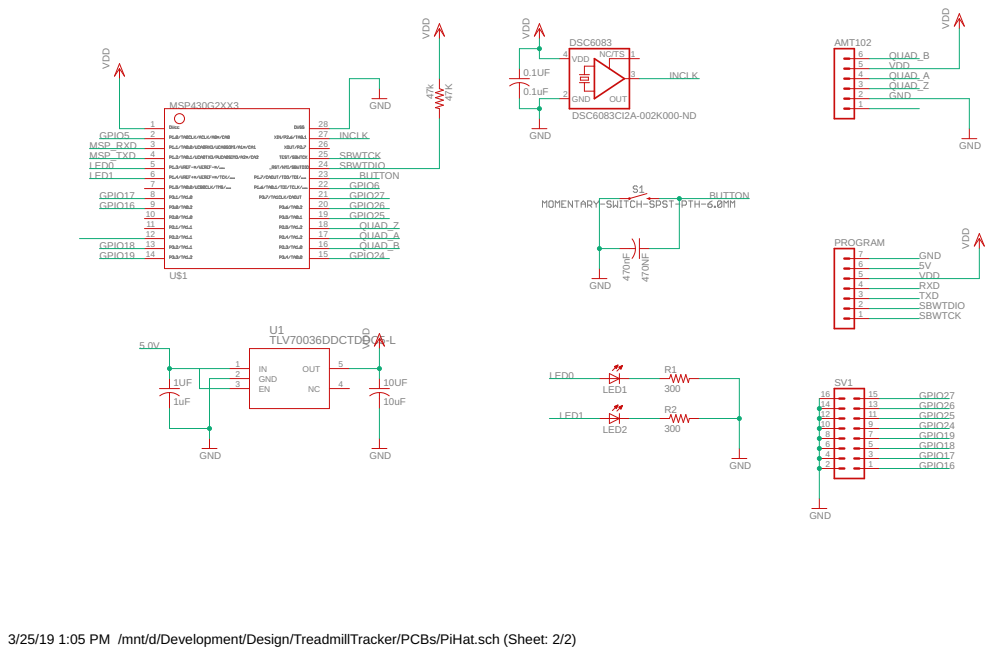
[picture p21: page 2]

3/25/19 1:05 PM /mnt/d/Development/Design/TreadmillTracker/PCBs/PiHat.sch (Sheet: 2/2)

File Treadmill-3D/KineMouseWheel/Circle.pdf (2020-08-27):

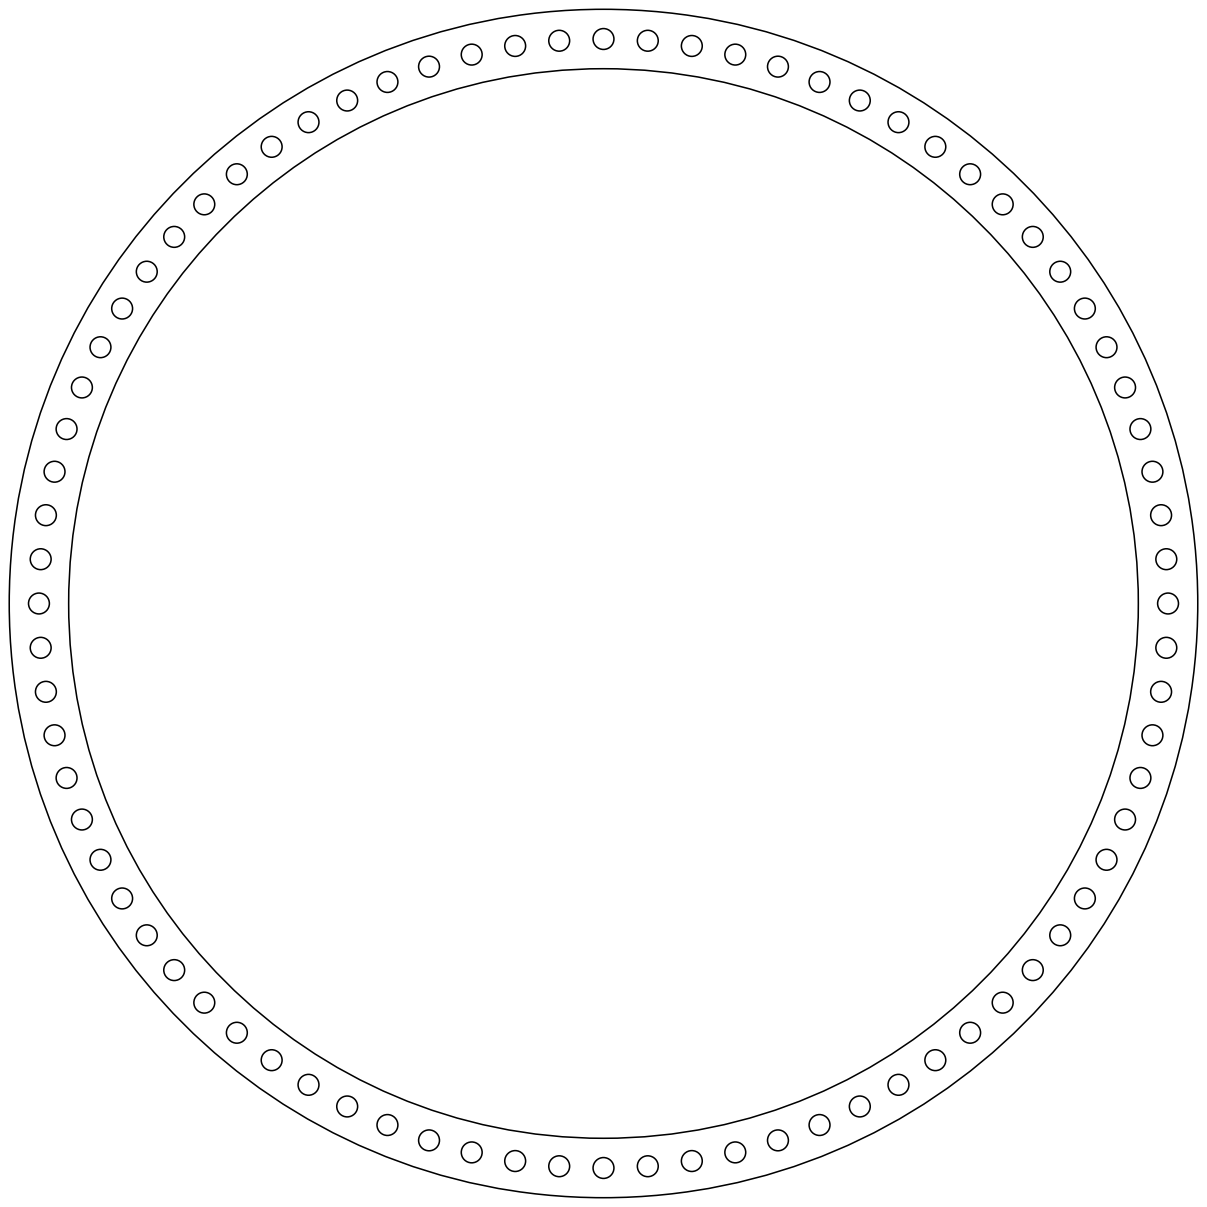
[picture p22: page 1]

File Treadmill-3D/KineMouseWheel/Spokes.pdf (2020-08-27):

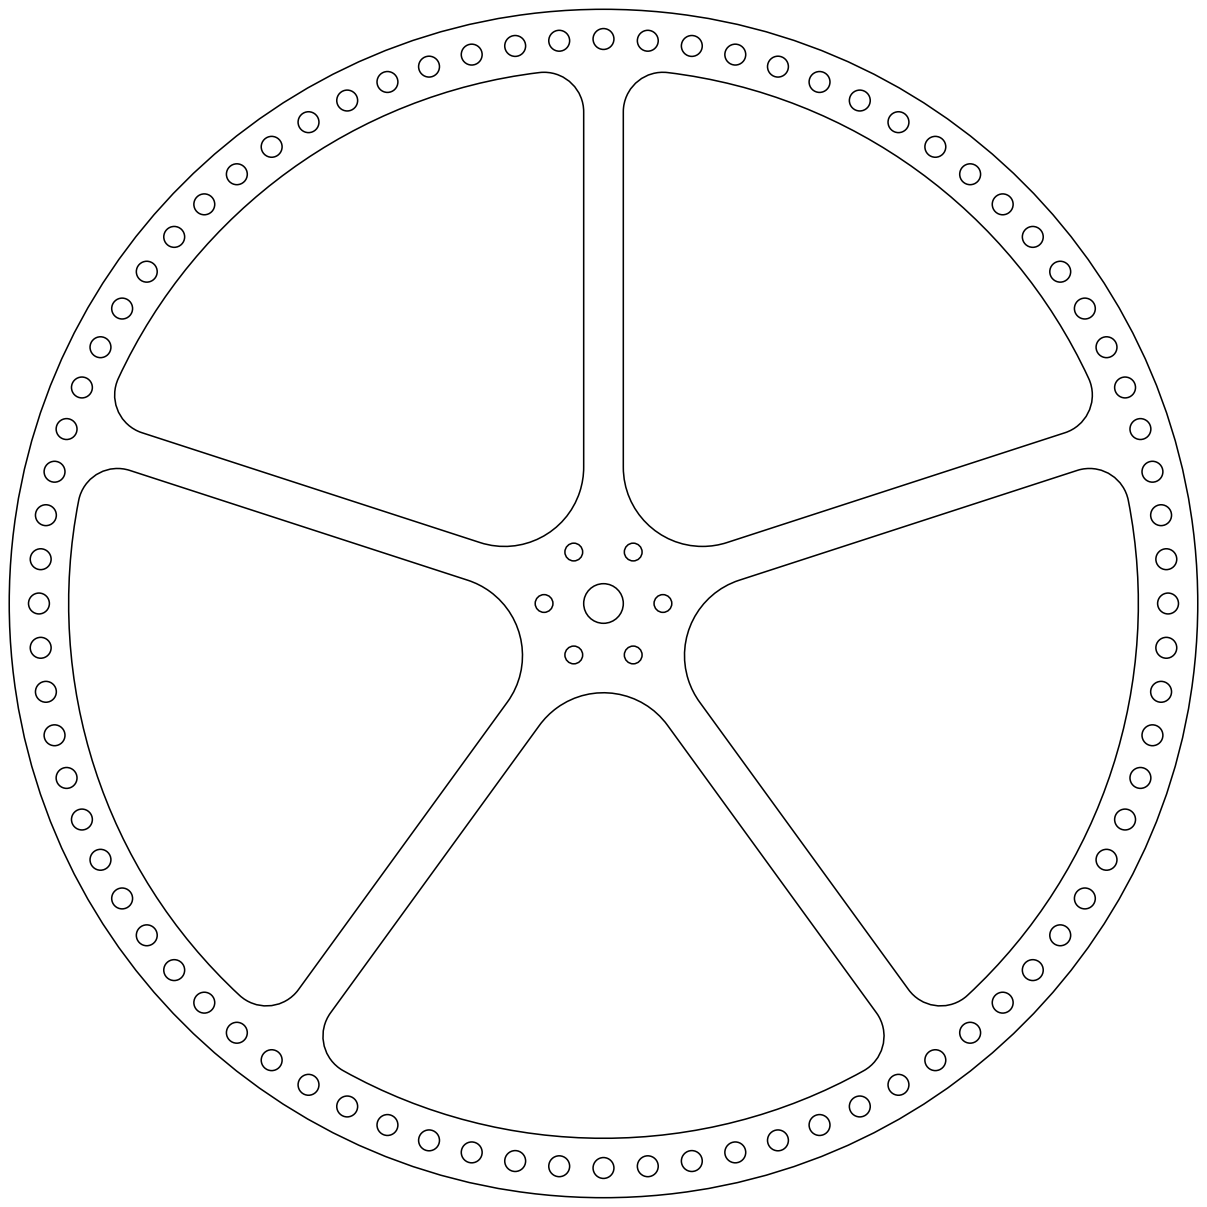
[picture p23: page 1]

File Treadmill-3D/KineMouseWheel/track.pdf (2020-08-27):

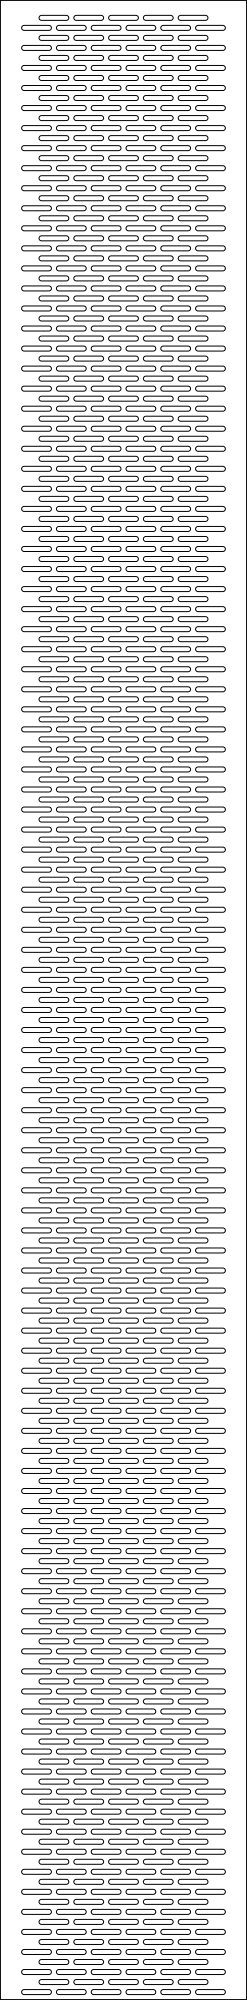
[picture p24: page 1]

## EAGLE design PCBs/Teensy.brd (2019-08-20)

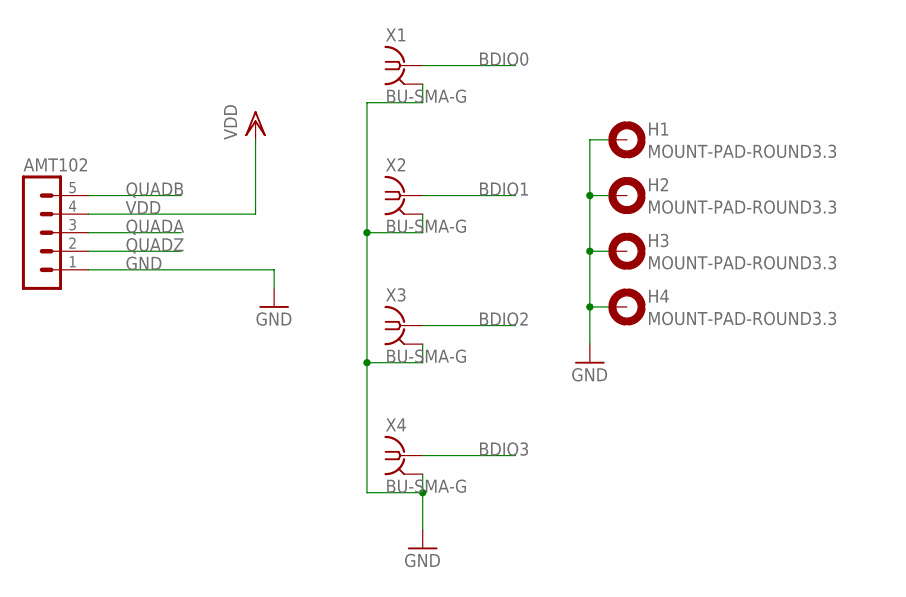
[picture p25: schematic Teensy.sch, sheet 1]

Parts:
AMT102: MA05-1
H1, H2, H3, H4: MOUNT-PAD-ROUND3.3; 3,3-PAD
X1, X2, X3, X4: BU-SMA-G

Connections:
BDIO0: X1.1; also elsewhere on the board
BDIO1: X2.1; also elsewhere on the board
BDIO2: X3.1; also elsewhere on the board
BDIO3: X4.1; also elsewhere on the board
GND: AMT102.1, H1.B3,3, H2.B3,3, H3.B3,3, H4.B3,3, X1.2, X1.3 (2), X1.4 (2), X1.5 (2), X2.2, X2.3 (2), X2.4 (2), X2.5 (2), X3.2, X3.3 (2), X3.4 (2), X3.5 (2), X4.2, X4.3 (2), X4.4 (2), X4.5 (2); also elsewhere on the board
QUADA: AMT102.3; also elsewhere on the board
QUADB: AMT102.5; also elsewhere on the board
QUADZ: AMT102.2; also elsewhere on the board
VDD: AMT102.4; also elsewhere on the board

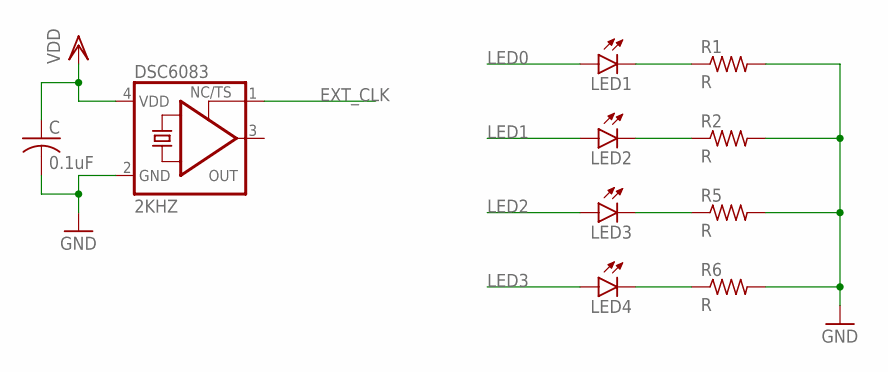
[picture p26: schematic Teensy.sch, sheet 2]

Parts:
C: 0.1uF; C0603
DSC6083: 2KHZ; 3.2X2.5_KXO-V96
LED1: LEDCHIPLED_0603; CHIPLED_0603
LED2, LED3, LED4: LEDCHIP-LED0603; CHIP-LED0603
R1, R2, R5, R6: R; R0603

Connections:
EXT_CLK: DSC6083.1 (TS); also elsewhere on the board
GND: C.2, DSC6083.2 (GND), R1.2, R2.2, R5.2, R6.2; also elsewhere on the board
LED0: LED1.A; also elsewhere on the board
LED1: LED2.A; also elsewhere on the board
LED2: LED3.A; also elsewhere on the board
LED3: LED4.A; also elsewhere on the board
unnamed: LED1.C, R1.1
unnamed: LED2.C, R2.1
unnamed: LED3.C, R5.1
unnamed: LED4.C, R6.1
VDD: C.1, DSC6083.4 (VDD); also elsewhere on the board

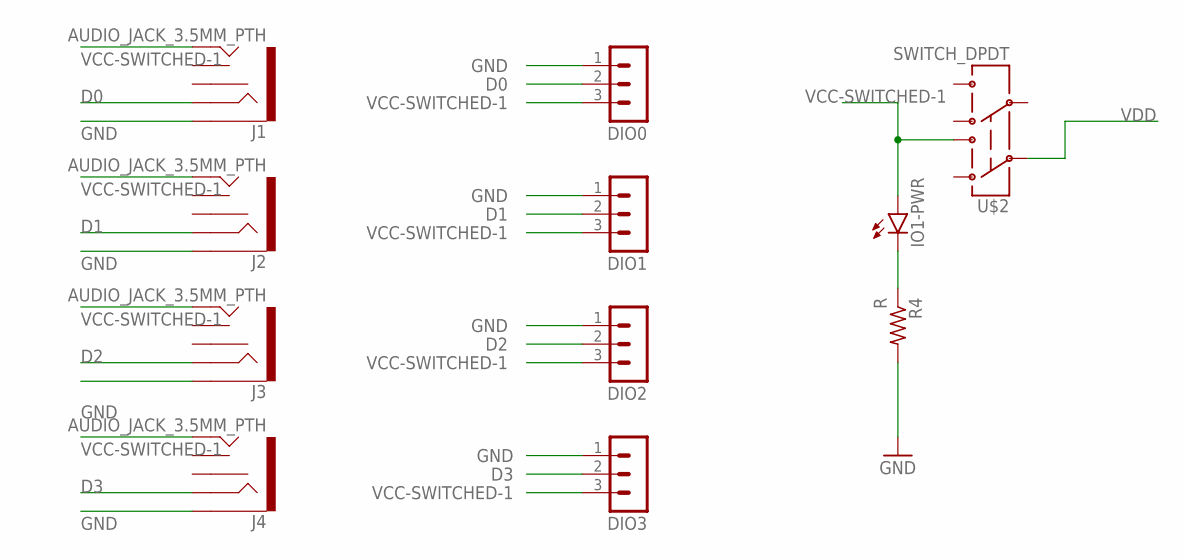
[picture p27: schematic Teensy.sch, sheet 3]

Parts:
DIO0, DIO1, DIO2, DIO3: MA03-1
IO1-PWR: LEDCHIP-LED0603; CHIP-LED0603
J1, J2, J3, J4: AUDIO_JACK_3.5MM_PTH; AUDIO-JACK
R4: R; R0603
U$2: SWITCH_DPDT; JS_DPDT_TH

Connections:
D0: DIO0.2, J1.RING; also elsewhere on the board
D1: DIO1.2, J2.RING; also elsewhere on the board
D2: DIO2.2, J3.RING; also elsewhere on the board
D3: DIO3.2, J4.RING; also elsewhere on the board
GND: DIO0.1, DIO1.1, DIO2.1, DIO3.1, J1.SLEEVE, J2.SLEEVE, J3.SLEEVE, J4.SLEEVE, R4.2; also elsewhere on the board
unnamed: IO1-PWR.C, R4.1
VCC-SWITCHED-1: DIO0.3, DIO1.3, DIO2.3, DIO3.3, IO1-PWR.A, J1.TIP, J2.TIP, J3.TIP, J4.TIP, U$2.3
VDD: U$2.2; also elsewhere on the board

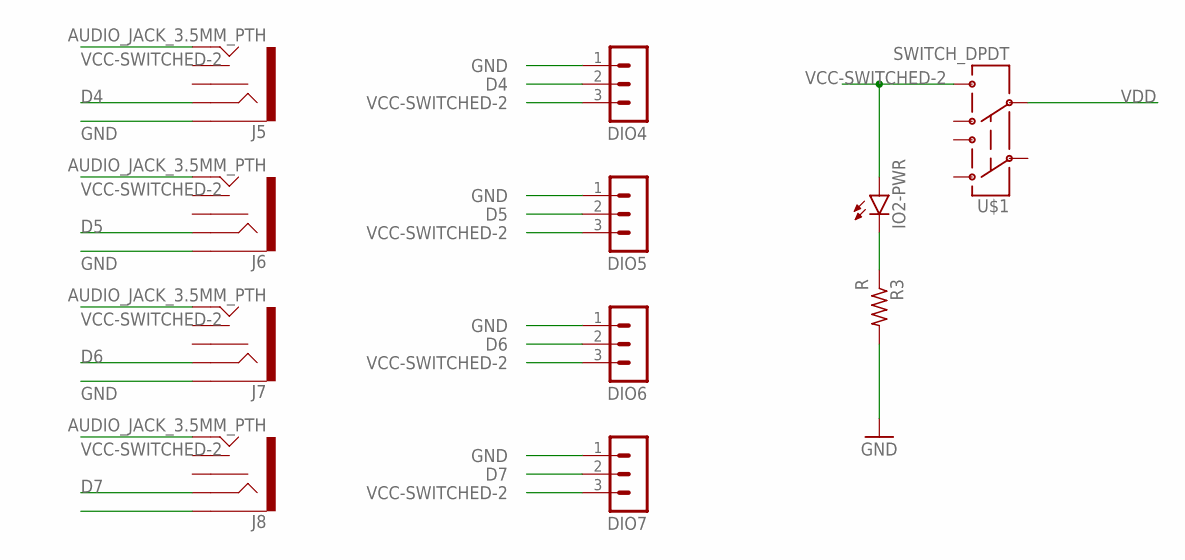
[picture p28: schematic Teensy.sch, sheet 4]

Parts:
DIO4, DIO5, DIO6, DIO7: MA03-1
IO2-PWR: LEDCHIP-LED0603; CHIP-LED0603
J5, J6, J7, J8: AUDIO_JACK_3.5MM_PTH; AUDIO-JACK
R3: R; R0603
U$1: SWITCH_DPDT; JS_DPDT_TH

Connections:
D4: DIO4.2, J5.RING; also elsewhere on the board
D5: DIO5.2, J6.RING; also elsewhere on the board
D6: DIO6.2, J7.RING; also elsewhere on the board
D7: DIO7.2, J8.RING; also elsewhere on the board
GND: DIO4.1, DIO5.1, DIO6.1, DIO7.1, J5.SLEEVE, J6.SLEEVE, J7.SLEEVE, J8.SLEEVE, R3.2; also elsewhere on the board
unnamed: IO2-PWR.C, R3.1
VCC-SWITCHED-2: DIO4.3, DIO5.3, DIO6.3, DIO7.3, IO2-PWR.A, J5.TIP, J6.TIP, J7.TIP, J8.TIP, U$1.6
VDD: U$1.5; also elsewhere on the board

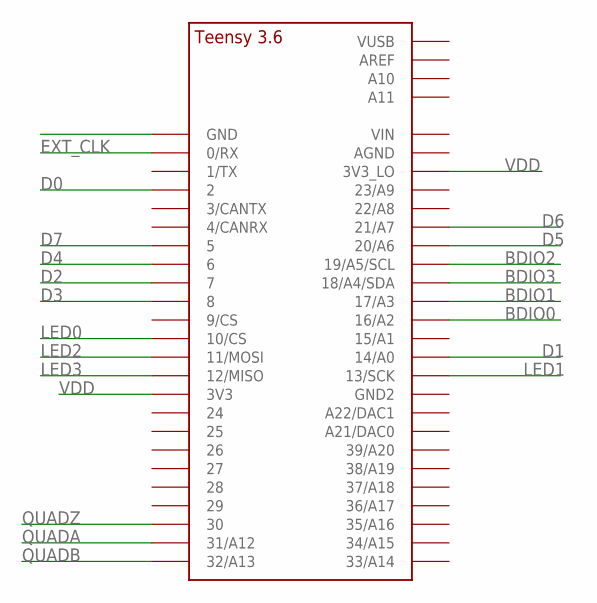
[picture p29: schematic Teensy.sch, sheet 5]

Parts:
U$3: TEENSY_3.5/3.6_BASIC

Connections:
BDIO0: U$3.16/A2; also elsewhere on the board
BDIO1: U$3.17/A3; also elsewhere on the board
BDIO2: U$3.19/A5/SCL; also elsewhere on the board
BDIO3: U$3.18/A4/SDA; also elsewhere on the board
D0: U$3.2; also elsewhere on the board
D1: U$3.14/A0; also elsewhere on the board
D2: U$3.7; also elsewhere on the board
D3: U$3.8; also elsewhere on the board
D4: U$3.6; also elsewhere on the board
D5: U$3.20/A6; also elsewhere on the board
D6: U$3.21/A7; also elsewhere on the board
D7: U$3.5; also elsewhere on the board
EXT_CLK: U$3.0/RX; also elsewhere on the board
GND: U$3.GND; also elsewhere on the board
LED0: U$3.10/CS; also elsewhere on the board
LED1: U$3.13/SCK; also elsewhere on the board
LED2: U$3.11/MOSI; also elsewhere on the board
LED3: U$3.12/MISO; also elsewhere on the board
QUADA: U$3.31/A12; also elsewhere on the board
QUADB: U$3.32/A13; also elsewhere on the board
QUADZ: U$3.30; also elsewhere on the board
VDD: U$3.3V3, U$3.3V3_LO; also elsewhere on the board

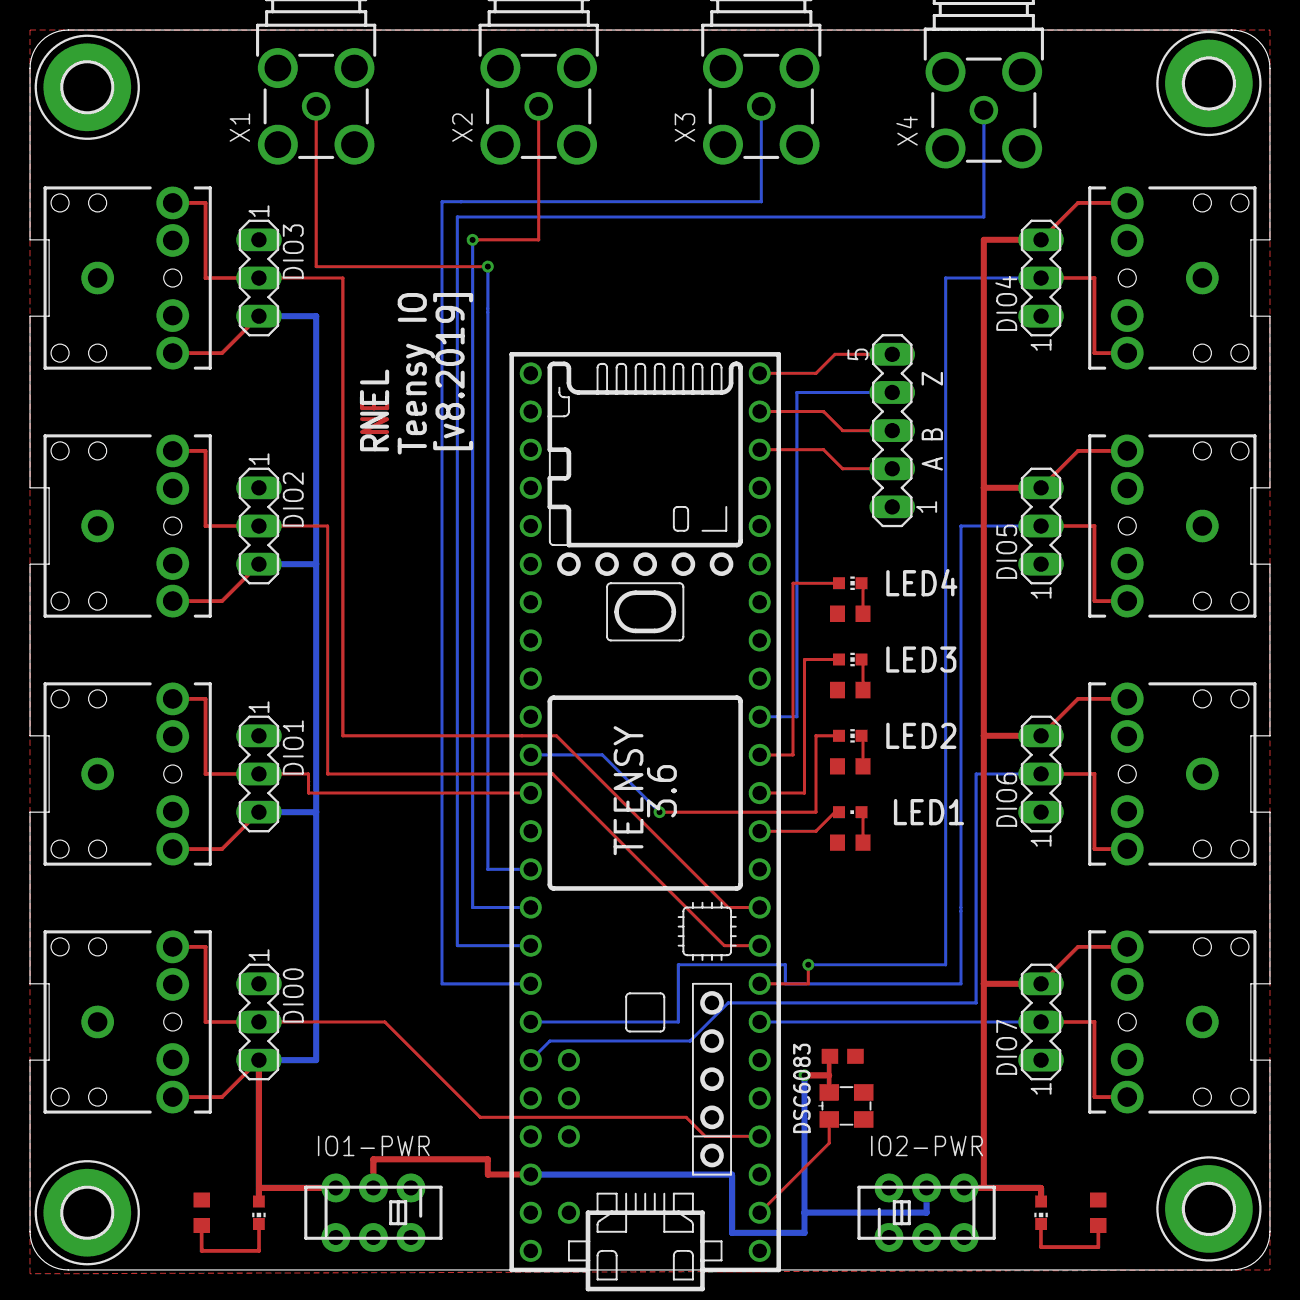
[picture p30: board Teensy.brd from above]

Board: 2 copper layers, 82.5 x 82.5 mm, 42 parts (0 on the bottom side), 30 nets.

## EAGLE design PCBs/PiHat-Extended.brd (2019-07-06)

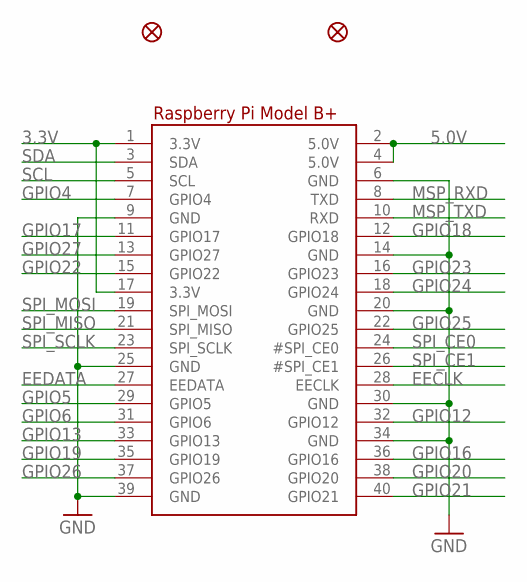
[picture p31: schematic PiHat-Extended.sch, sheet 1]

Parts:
FID2, FID3: MICROBUILDER_FIDUCIAL""; MICROBUILDER_FIDUCIAL_1MM
RPI1: MICROBUILDER_RASPBERRYPI_BPLUS_HATNOSLOTS; MICROBUILDER_PI_HAT_NOSLOTS

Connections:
3.3V: RPI1.1 (3.3V), RPI1.17 (3.3V)
5.0V: RPI1.2 (5.0V), RPI1.4 (5.0V); also elsewhere on the board
EECLK: RPI1.28 (EECLK)
EEDATA: RPI1.27 (EEDATA)
GND: RPI1.6 (GND), RPI1.9 (GND), RPI1.14 (GND), RPI1.20 (GND), RPI1.25 (GND), RPI1.30 (GND), RPI1.34 (GND), RPI1.39 (GND); also elsewhere on the board
GPIO4: RPI1.7 (GPIO4)
GPIO5: RPI1.29 (GPIO5); also elsewhere on the board
GPIO6: RPI1.31 (GPIO6); also elsewhere on the board
GPIO12: RPI1.32 (GPIO12)
GPIO13: RPI1.33 (GPIO13)
GPIO16: RPI1.36 (GPIO16); also elsewhere on the board
GPIO17: RPI1.11 (GPIO17); also elsewhere on the board
GPIO18: RPI1.12 (GPIO18)
GPIO19: RPI1.35 (GPIO19)
GPIO20: RPI1.38 (GPIO20)
GPIO21: RPI1.40 (GPIO21)
GPIO22: RPI1.15 (GPIO22); also elsewhere on the board
GPIO23: RPI1.16 (GPIO23); also elsewhere on the board
GPIO24: RPI1.18 (GPIO24); also elsewhere on the board
GPIO25: RPI1.22 (GPIO25); also elsewhere on the board
GPIO26: RPI1.37 (GPIO26); also elsewhere on the board
GPIO27: RPI1.13 (GPIO27); also elsewhere on the board
MSP_RXD: RPI1.8 (TXD); also elsewhere on the board
MSP_TXD: RPI1.10 (RXD); also elsewhere on the board
SCL: RPI1.5 (SCL)
SDA: RPI1.3 (SDA)
SPI_CE0: RPI1.24 (#SPI_CE0)
SPI_CE1: RPI1.26 (#SPI_CE1)
SPI_MISO: RPI1.21 (SPI_MISO)
SPI_MOSI: RPI1.19 (SPI_MOSI)
SPI_SCLK: RPI1.23 (SPI_SCLK)

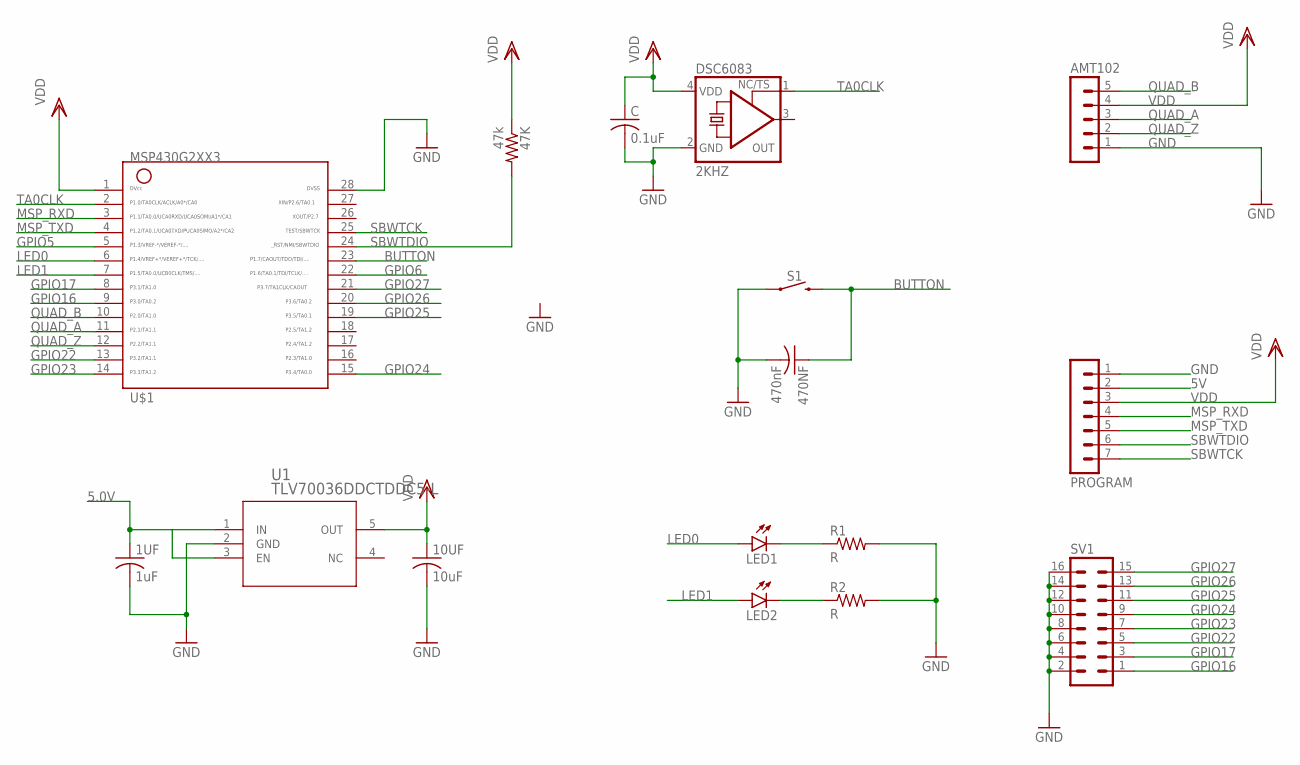
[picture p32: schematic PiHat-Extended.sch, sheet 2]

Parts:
1UF: 1uF; C0603
10UF: 10uF; C1206
47K: 47k; R0603
470NF: 470nF; C0603
AMT102: MA05-1
C: 0.1uF; C0603
DSC6083: 2KHZ; 3.2X2.5_KXO-V96
LED1, LED2: LEDCHIPLED_1206; CHIPLED_1206
PROGRAM: MA07-1
R1, R2: R; R0603
S1: MOMENTARY-SWITCH-SPST-PTH-6.0MM; TACTILE_SWITCH_PTH_6.0MM
SV1: MA08-2
U1: TLV70036DDCTDDC5-L; DDC5-L
U$1: MSP430; PW28

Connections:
5.0V: 1UF.1, U1.1 (IN), U1.3 (EN); also elsewhere on the board
5V: PROGRAM.2
BUTTON: 470NF.1, S1.3 (2), U$1.23
GND: 1UF.2, 10UF.2, 470NF.2, AMT102.1, C.2, DSC6083.2 (GND), PROGRAM.1, R1.2, R2.2, S1.1, SV1.2, SV1.4, SV1.6, SV1.8, SV1.10, SV1.12, SV1.14, SV1.16, U1.2 (GND), U$1.28; also elsewhere on the board
GPIO5: U$1.5; also elsewhere on the board
GPIO6: U$1.22; also elsewhere on the board
GPIO16: SV1.1, U$1.9; also elsewhere on the board
GPIO17: SV1.3, U$1.8; also elsewhere on the board
GPIO22: SV1.5, U$1.13; also elsewhere on the board
GPIO23: SV1.7, U$1.14; also elsewhere on the board
GPIO24: SV1.9, U$1.15; also elsewhere on the board
GPIO25: SV1.11, U$1.19; also elsewhere on the board
GPIO26: SV1.13, U$1.20; also elsewhere on the board
GPIO27: SV1.15, U$1.21; also elsewhere on the board
LED0: LED1.A, U$1.6
LED1: LED2.A, U$1.7
MSP_RXD: PROGRAM.4, U$1.3; also elsewhere on the board
MSP_TXD: PROGRAM.5, U$1.4; also elsewhere on the board
unnamed: LED1.C, R1.1
unnamed: LED2.C, R2.1
QUAD_A: AMT102.3, U$1.11
QUAD_B: AMT102.5, U$1.10
QUAD_Z: AMT102.2, U$1.12
SBWTCK: PROGRAM.7, U$1.25
SBWTDIO: 47K.2, PROGRAM.6, U$1.24
TA0CLK: DSC6083.1 (TS), U$1.2
VDD: 10UF.1, 47K.1, AMT102.4, C.1, DSC6083.4 (VDD), PROGRAM.3, U1.5 (OUT), U$1.1; also elsewhere on the board

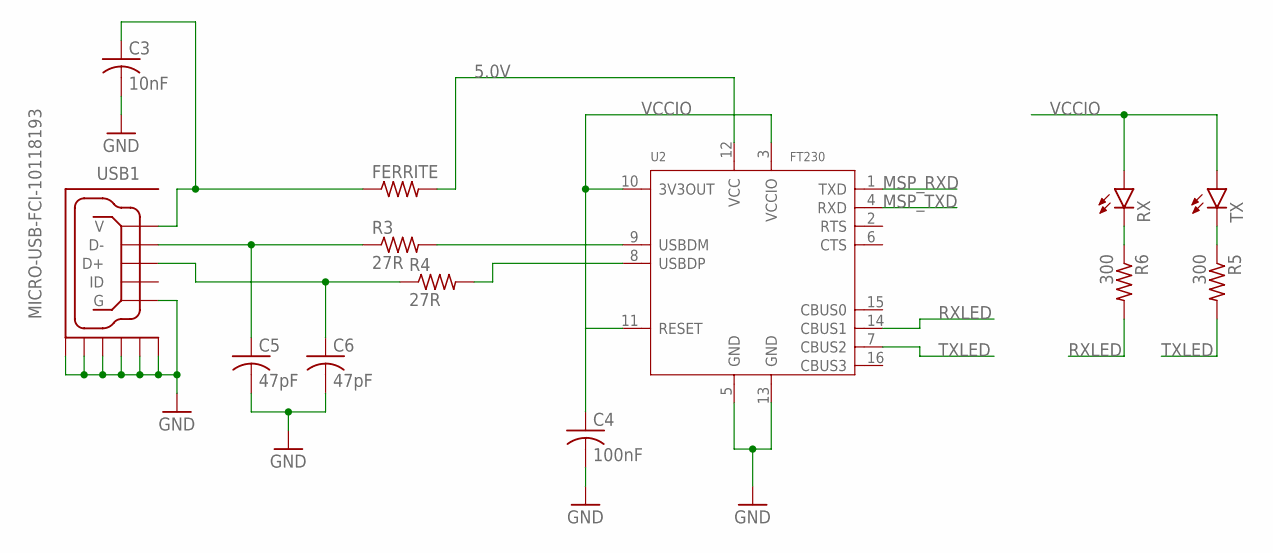
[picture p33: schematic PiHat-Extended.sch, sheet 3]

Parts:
C3: 10nF; C0603
C4: 100nF; C0603
C5, C6: 47pF; C0603
FERRITE: R-US_R0805; R0805
R3, R4: 27R; R0603
R5, R6: 300; R0603
RX: LEDCHIPLED_1206; CHIPLED_1206
TX: LEDCHIPLED_1206; CHIPLED_1206
U2: FT230; SSOP16-0.635-5X4MM
USB1: MICRO-USB-FCI-10118193; FCI-10118193-0001LF

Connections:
5.0V: FERRITE.2, U2.12 (VCC); also elsewhere on the board
GND: C3.2, C4.2, C5.2, C6.2, U2.5 (GND), U2.13 (GND), USB1.5 (G), USB1.G1 (GND1), USB1.G2 (GND2), USB1.G3 (GND3), USB1.G4 (GND4), USB1.G5 (GND5), USB1.G6 (GND6); also elsewhere on the board
MSP_RXD: U2.1 (TXD); also elsewhere on the board
MSP_TXD: U2.4 (RXD); also elsewhere on the board
unnamed: C3.1, FERRITE.1, USB1.1 (V)
unnamed: C5.1, R3.1, USB1.2 (D-)
unnamed: R3.2, U2.9 (USBDM)
unnamed: C6.1, R4.1, USB1.3 (D+)
unnamed: R4.2, U2.8 (USBDP)
unnamed: R6.1, RX.C
unnamed: R5.1, TX.C
RXLED: R6.2, U2.14 (CBUS1)
TXLED: R5.2, U2.7 (CBUS2)
VCCIO: C4.1, RX.A, TX.A, U2.3 (VCCIO), U2.10 (3V3OUT), U2.11 (RESET)

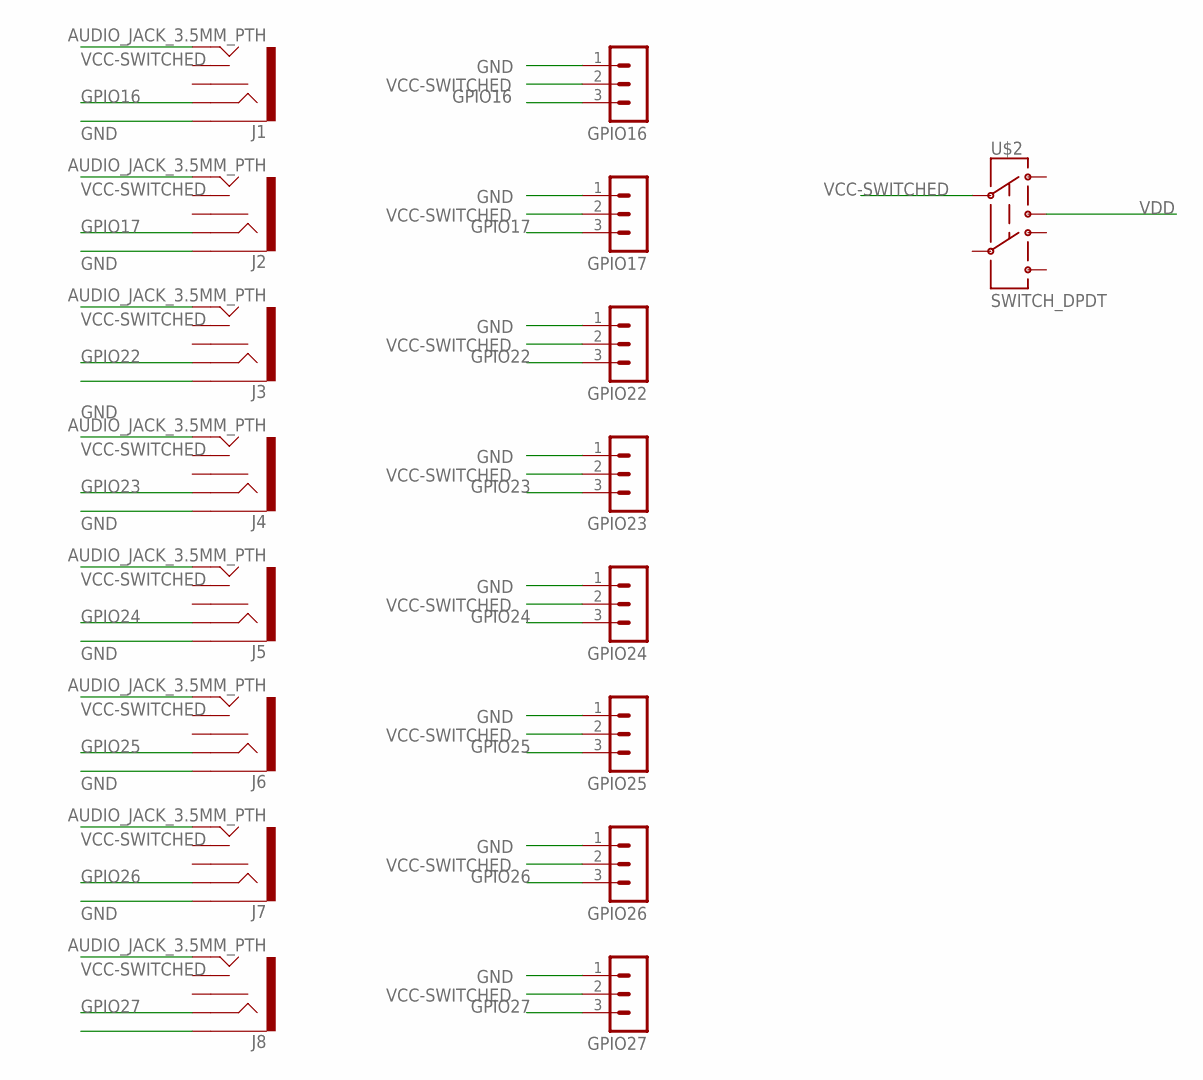
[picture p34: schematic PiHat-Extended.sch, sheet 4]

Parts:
GPIO16, GPIO17, GPIO22, GPIO23, GPIO24, GPIO25, GPIO26, GPIO27: MA03-1
J1, J2, J3, J4, J5, J6, J7, J8: AUDIO_JACK_3.5MM_PTH; AUDIO-JACK
U$2: SWITCH_DPDT; JS_DPDT_TH

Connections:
GND: GPIO16.1, GPIO17.1, GPIO22.1, GPIO23.1, GPIO24.1, GPIO25.1, GPIO26.1, GPIO27.1, J1.SLEEVE, J2.SLEEVE, J3.SLEEVE, J4.SLEEVE, J5.SLEEVE, J6.SLEEVE, J7.SLEEVE, J8.SLEEVE; also elsewhere on the board
GPIO16: GPIO16.3, J1.RING; also elsewhere on the board
GPIO17: GPIO17.3, J2.RING; also elsewhere on the board
GPIO22: GPIO22.3, J3.RING; also elsewhere on the board
GPIO23: GPIO23.3, J4.RING; also elsewhere on the board
GPIO24: GPIO24.3, J5.RING; also elsewhere on the board
GPIO25: GPIO25.3, J6.RING; also elsewhere on the board
GPIO26: GPIO26.3, J7.RING; also elsewhere on the board
GPIO27: GPIO27.3, J8.RING; also elsewhere on the board
VCC-SWITCHED: GPIO16.2, GPIO17.2, GPIO22.2, GPIO23.2, GPIO24.2, GPIO25.2, GPIO26.2, GPIO27.2, J1.TIP, J2.TIP, J3.TIP, J4.TIP, J5.TIP, J6.TIP, J7.TIP, J8.TIP, U$2.2
VDD: U$2.3; also elsewhere on the board

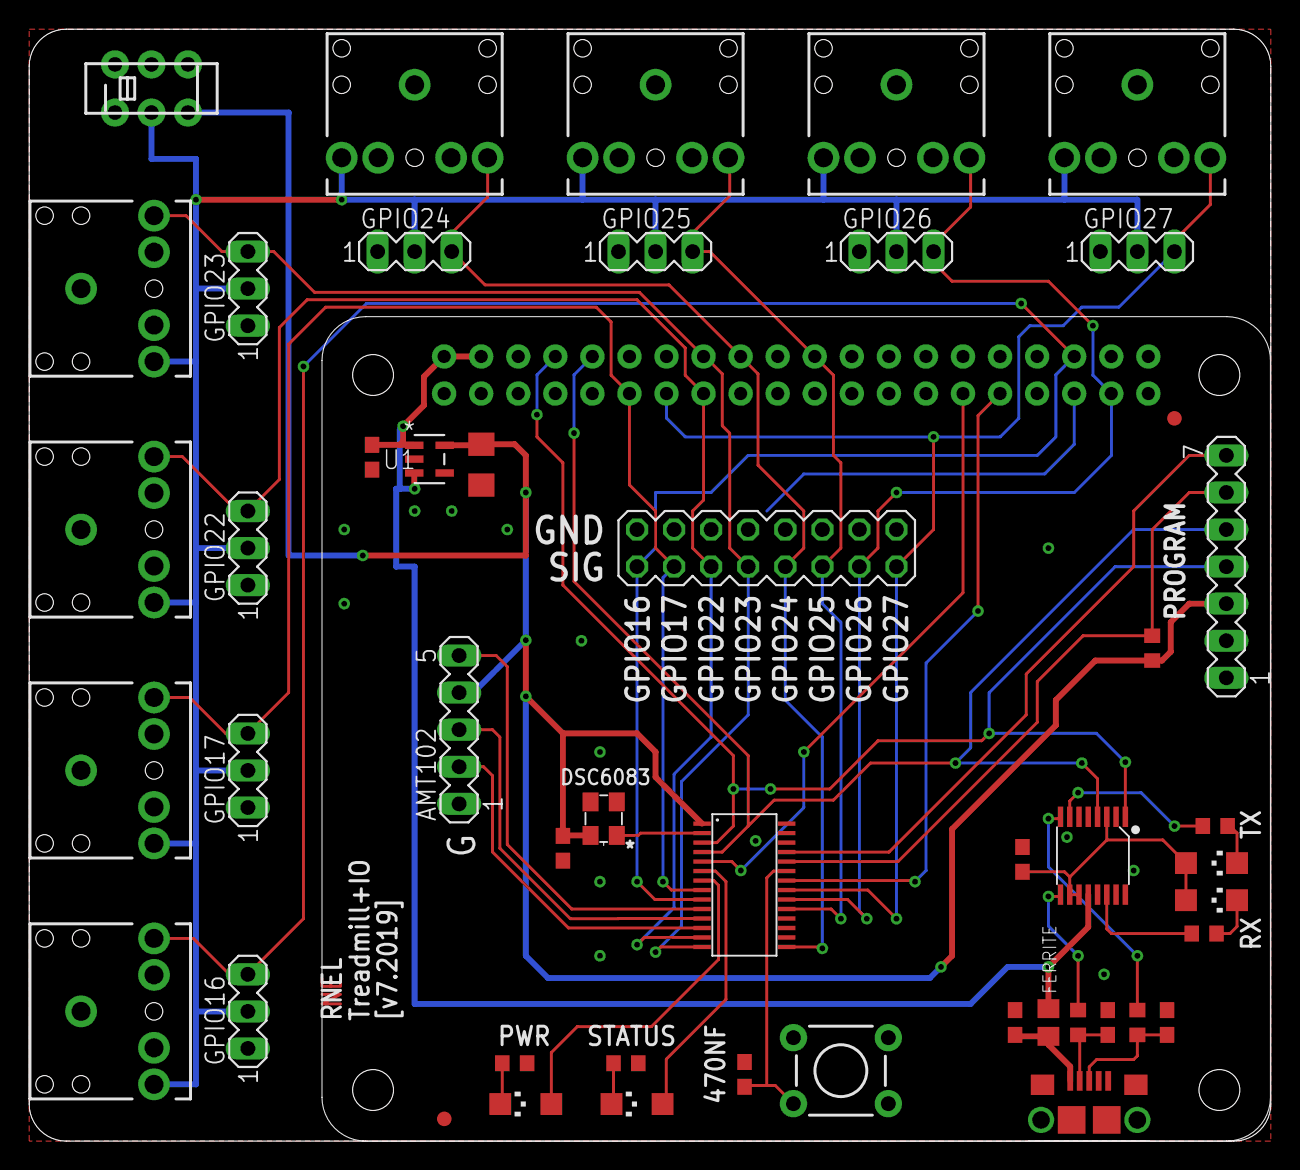
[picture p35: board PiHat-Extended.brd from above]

Board: 2 copper layers, 85.1 x 76.2 mm, 49 parts (0 on the bottom side), 38 nets.

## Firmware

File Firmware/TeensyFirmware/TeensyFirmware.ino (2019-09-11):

#define CLOCK_PIN 0 // B16

#define QUADZ 30 // C11
#define QUADA 31 // E0
#define QUADB 32 // B18

#define BDIO0 16 // B0
#define BDIO1 17 // B1
#define BDIO2 19 // B2
#define BDIO3 18 // B3

#define D0 2 // D0
#define D1 14 // ...
#define D2 7
#define D3 8
#define D4 6
#define D5 20
#define D6 21
#define D7 5 // D7

#define LED0 10 //PIN_C4;
#define LED1 13 //PIN_C5;
#define LED2 11 //PIN_C6;
#define LED3 12 //PIN_C7;

#define ENCODER_OPTIMIZE_INTERRUPTS // this messes up attachInterrupts
#include <Encoder.h>


IntervalTimer sendDataTimer;

Encoder wheelPosition(QUADA, QUADB);

uint32_t ledState = 0x11111111;

struct _TreadmillDataStruct {
  char StartChar;
  char DataLength;
//  uint16_t MasterClockLow;
//  uint16_t MasterClockHigh;
  uint32_t MasterClock;
  int16_t  EncoderTicks;
  int32_t  UnwrappedEncoderTicks;
  uint8_t  GPIO;
  char EndChar;
} __attribute__((packed));
typedef struct _TreadmillDataStruct TreadmillDataStruct;

TreadmillDataStruct TreadmillData;

volatile uint32_t MasterClock = 0;

boolean SerialTransmitFlag = false;

// ISR routine for FlexTimer1 Module
extern "C" void ftm1_isr(void) {
  if ((FTM1_SC & FTM_SC_TOF) != 0) {  //read the timer overflow flag (TOF in FTM1_SC)
    MasterClock++;
    FTM1_SC &= ~FTM_SC_TOF;           //if set, clear overflow flag

    if ((MasterClock & 0x01) == 0)
      SerialTransmitFlag  = true;
  }
}

void sendData() {

  if (Serial.dtr()) {
    TreadmillData.MasterClock = MasterClock;
    TreadmillData.GPIO = GPIOD_PDIR;
    TreadmillData.UnwrappedEncoderTicks = wheelPosition.read();
    Serial.write((char *) &TreadmillData, sizeof(TreadmillDataStruct));
    Serial.flush();
  }

/*
  if ((MasterClock & 0x3F) == 0) {
    GPIOC_PDOR = ledState & 0xF0;
    ledState = (ledState << 1) | (ledState >> 31);
  }*/
}


void setup() {
  pinMode(LED0, OUTPUT);
  pinMode(LED1, OUTPUT);
  pinMode(LED2, OUTPUT);
  pinMode(LED3, OUTPUT);
  digitalWrite(LED0,0);
  digitalWrite(LED1,0);
  digitalWrite(LED2,0);
  digitalWrite(LED3,0);

  //GPIOD_PDDR = GPIOC_PDDR & ~0xFF00; // set pins 0-7 to output
  pinMode(D0, INPUT);
  pinMode(D1, INPUT);
  pinMode(D2, INPUT);
  pinMode(D3, INPUT);
  pinMode(D4, OUTPUT);
  pinMode(D5, OUTPUT);
  pinMode(D6, OUTPUT);
  pinMode(D7, OUTPUT);
  digitalWrite(D4, 0);
  digitalWrite(D5, 0);
  digitalWrite(D6, 0);
  digitalWrite(D7, 0);
  
  TreadmillData.StartChar = 'E';
  TreadmillData.EndChar = '\n';
  TreadmillData.DataLength = sizeof(TreadmillDataStruct);

  /* 
   *  Set up FTM timer module which connects to external 2kHz
   *   clock for master timing. The clock is set up both to increment
   *   the master clock counter. When it overflows, this also triggers
   *   the high 16 bits of the master clock to increment.
   *   
   *   Note that unlike with the MSP430, we can't independently set
   *   a second interrupt to trigger every millisecond to drive serial
   *   data transmission, so we'll just use the Teensy for that.
   *   
   */
  CORE_PIN0_CONFIG = PORT_PCR_MUX(4);
  NVIC_DISABLE_IRQ(IRQ_FTM1);
  FTM1_SC = 0;
  FTM1_CNT = 0;
  FTM1_MOD = 0x1; // set to overflow every two ticks (1 kHz)
  FTM1_SC = FTM_SC_CLKS(3) + FTM_SC_PS(0) + FTM_SC_TOIE; // External clock input
  NVIC_ENABLE_IRQ(IRQ_FTM1);
  
  Serial.begin(256000);
  //sendDataTimer.begin(sendData, 2000); // 2 ms
}


void loop() {
  // put your main code here, to run repeatedly:
  interrupts();
  if (SerialTransmitFlag) {
    sendData();
    SerialTransmitFlag = false; // I'm worried about the case where I set this right when the timer is trying to wake us up.
                                // But I guess in that case, it would indicate we're on the hairy edge of stability, which is bad anyway.
  }
  if (Serial.available()) {
    uint8_t incomingByte = Serial.read();  // will not be -1
    GPIOD_PDOR = incomingByte & 0xF0; // Recalling that higher order bits are output
    GPIOC_PDOR = incomingByte & 0xF0; // Recalling that higher order bits are output
  }
}

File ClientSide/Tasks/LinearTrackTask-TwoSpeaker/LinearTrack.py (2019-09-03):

#!/usr/bin/env python

# Imports
import time
import struct
import os
import argparse
import json
import datetime
from shutil import copy
import numpy as np
import csv
from enum import Enum, auto, unique
from subprocess import Popen, DEVNULL
from Interface import SerialInterface, Sounds, Camera

# Command-line arguments: computer settings
parser = argparse.ArgumentParser(description='Run simple linear track experiment.')
parser.add_argument('-P', '--serial-port', default='/dev/ttyS0',
                   help='TTY device for USB-serial interface (e.g., /dev/ttyUSB0 or COM10)')
parser.add_argument('-O', '--osc-port', type=int, default=12345, 
                   help='Serial port for OSC client')
parser.add_argument('--prefix', default='Data Log - ',
                   help='Prefix for output file - defaults to [Data Log - ]')
parser.add_argument('--param-file', default='defaults.json',
                    help='JSON file containing task parameters')
parser.add_argument('--output-dir', default='./',
                    help='Directory to write output file (defaults to cwd)')
args = parser.parse_args()
if not os.path.isdir(args.output_dir):
    os.mkdir(args.output_dir)
if not args.output_dir.endswith('/'):
    args.output_dir += '/'

# JSON parameters: task settings
with open(args.param_file) as f:
    d = json.loads(f.read())

    # General info
    mouseID = d['Info']['MouseID']
    sessionID = d['Info']['Session']
    GPIO_IDs = d['Info']['GPIO_IDs'] # GPIO IDs on Hat
    if not (GPIO_IDs[-1] == -1):
        # Add [-1] at end to avoid using unused GPIO logic
        GPIO_IDs.append(-1)

    # Sound timing
    FirstBetweenDispensingDelay = d['Delay']['FirstBetweenDispensingDelay']
    PreDispenseToneDelay = d['Delay']['PreDispenseToneDelay']
    PostDispenseDelay = d['Delay']['PostDispenseDelay']
    PostDispenseToneDelay = d['Delay']['PostDispenseToneDelay']
    SubsequentBetweenDispensingDelay = d['Delay']['SubsequentBetweenDispensingDelay']
    PokeEntryDelay = d['Delay']['PokeEntryDelay']
    PokeExitDelay = d['Delay']['PokeExitDelay']

    # Sound settings
    PinkNoiseParams = d['Sound']['PinkNoise']
    ToneCloudParams = d['Sound']['ToneCloud']
    ToneParams = d['Sound']['Tone']

    # GPIO configuration
    LeftPokeGPIO = d['GPIO']['LeftPoke']
    RightPokeGPIO = d['GPIO']['RightPoke']
    LeftLickGPIO = d['GPIO']['LeftLick']
    RightLickGPIO = d['GPIO']['RightLick']
    LeftDispenseGPIO = d['GPIO']['LeftDispense']
    RightDispenseGPIO = d['GPIO']['RightDispense']

    # Reward decay
    tau = d['Reward']['tau']
    r_0 = d['Reward']['r_0']
    R_0 = d['Reward']['R_0']

    # Camera settings
    camParams = {'fps': d['Camera']['fps'],
                 'resolution': d['Camera']['Resolution'],
                 'codec': d['Camera']['Codec'],
                 'audio': d['Camera']['Audio']}

# Save session parameters and set up data logging
dateString = datetime.datetime.now().strftime("%Y-%m-%d-%H%M")
newFilename = '{}_d{:02d}_{}_params.json'.format(mouseID, sessionID, dateString)
newFilepath = args.output_dir + newFilename
copy(args.param_file, newFilepath)
logFilename = '{}_d{:02d}_{}_log.txt'.format(mouseID, sessionID, dateString)
camFilename = '{}_d{:02d}_{}_cam'.format(mouseID, sessionID, dateString)

# Define logic classes
class MazeStates(Enum):
    NotPoked = auto()
    PokedLeft = auto()
    PokedRight = auto()
    PokedEither = auto()

@unique
class PokeSubstates(Enum):
    NotPoked = auto() # task logic state
    Exiting = auto() # sensor state (for smoothing)
    Entering = auto() # sensor state (for smoothing)
    BetweenDispensingDelay = auto()
    PreDispenseToneDelay = auto()
    PostDispenseDelay = auto()
    PostDispenseToneDelay = auto()

class WellData:
    # State logic: store as integer type
    LeftPokeMask = 2**(GPIO_IDs.index(LeftPokeGPIO))
    RightPokeMask = 2**(GPIO_IDs.index(RightPokeGPIO))
    LeftLickMask = 2**(GPIO_IDs.index(LeftLickGPIO))
    RightLickMask = 2**(GPIO_IDs.index(RightLickGPIO))

    # Serial data: store as binary string
    LeftDispenseMask = struct.pack('<B', 2**(GPIO_IDs.index(LeftDispenseGPIO)))
    RightDispenseMask = struct.pack('<B', 2**(GPIO_IDs.index(RightDispenseGPIO)))

# Initialize behavior logic
Well = WellData()
CurrentMazeState = MazeStates.NotPoked
ValidNextMazeState = MazeStates.PokedEither 
CurrentPokeState = PokeSubstates.NotPoked
DelayEnd = 0
ReentryState = [PokeSubstates.NotPoked, DelayEnd]
RewardNumber = 0
n = np.arange(int(tau*r_0/R_0))
tReward = -tau*np.log(1.0 - (n*R_0)/(tau*r_0)) * 1000 # ms
tDelay = np.append(np.diff(tReward), np.inf)

# Initialize sounds
PinkNoiseStim = Sounds(Name='PinkNoise', 
                       Channel=PinkNoiseParams['Channel'], 
                       OnVolume=PinkNoiseParams['OnVolume'], 
                       OffVolume=PinkNoiseParams['OffVolume'], 
                       OscPort=args.osc_port)
ToneCloudStim = Sounds(Name='ToneCloud', 
                       Channel=ToneCloudParams['Channel'], 
                       OnVolume=ToneCloudParams['OnVolume'], 
                       OffVolume=ToneCloudParams['OffVolume'], 
                       OscPort=args.osc_port)
ToneStim      = Sounds(Name='Tone', 
                       Channel=ToneParams['Channel'], 
                       OnVolume=ToneParams['OnVolume'], 
                       OffVolume=ToneParams['OffVolume'], 
                       OscPort=args.osc_port)

# Play sounds
print('Getting ready to start')
PinkNoiseStim.Stop()
ToneCloudStim.Stop()
ToneStim.Play()
time.sleep(1)
PinkNoiseStim.Stop()
ToneStim.Stop()
ToneCloudStim.Play()
time.sleep(1)
ToneCloudStim.Stop()
ToneStim.Stop()
PinkNoiseStim.Play()

# With the serial data stream, because the rate of transfer is so high, the input buffer will
# over flow quite rapidly. So the following chunk of code (which connects,  empties out the
# buffer and gets things aligned on individual messages) needs to be run as closely as possible
# to the actual start of data transfer!
print('Connecting to serial/USB interface {} and synchronizing.'.format(args.serial_port))

with open(args.output_dir + logFilename, 'w', newline='') as log_file,\
     Camera(args.output_dir + camFilename, **camParams) as cam:
    writer = csv.writer(log_file)
    Interface = SerialInterface(SerialPort=args.serial_port)
    while(True):
        #last_ts = time.time() 
        last_ts = time.monotonic()
        FlagChar, StructSize, MasterTime, Encoder, UnwrappedEncoder, GPIO = Interface.read_data()
        isPoked = int(CurrentMazeState in (MazeStates.PokedLeft, MazeStates.PokedRight))
        writer.writerow([MasterTime, last_ts, GPIO, isPoked])

        if (MasterTime % 1000) == 0:
            print('Heartbeat {} : 0x{:08b} '.format(MasterTime, GPIO))

        IsLeftWellPoked = (GPIO & Well.LeftPokeMask) == Well.LeftPokeMask
        IsRightWellPoked = (GPIO & Well.RightPokeMask) == Well.RightPokeMask

        if (IsLeftWellPoked and IsRightWellPoked):
            print('Flag: {}. Clocks: {}. Encoder: {}. Unwrapped: {}, GPIO: 0x{:08b}'.format(FlagChar, MasterTime, Encoder, UnwrappedEncoder, GPIO))
            raise Exception('Error: both Nose Pokes Activated')

        if CurrentMazeState in (MazeStates.PokedLeft, MazeStates.PokedRight):
            # Left Poke in Poked MazeState
            if not (IsLeftWellPoked or IsRightWellPoked):
                # Change poke state and set timer until NotPoked
                if CurrentPokeState != PokeSubstates.Exiting: 
                    ToneStim.Stop()
                    ReentryState = (CurrentPokeState, DelayEnd) # cache re-entry state
                    CurrentPokeState = PokeSubstates.Exiting
                    DelayEnd = MasterTime + PokeExitDelay
                # Change from poked to not if delay surpasssed
                elif (MasterTime > DelayEnd): # Change in state
                    print('Poked to not')
                    ToneCloudStim.Stop()
                    ToneStim.Stop()
                    PinkNoiseStim.Play()
                    DelayEnd = 0
                    RewardNumber = 0
                    CurrentPokeState = PokeSubstates.NotPoked
                    if CurrentMazeState == MazeStates.PokedLeft:
                        ValidNextMazeState = MazeStates.PokedRight
                        print('Next state right')
                    elif CurrentMazeState == MazeStates.PokedRight:
                        ValidNextMazeState = MazeStates.PokedLeft
                        print('Next state left')
                    CurrentMazeState = MazeStates.NotPoked

                continue

            # Reset to post-dispense state if re-entered before delay
            elif CurrentPokeState == PokeSubstates.Exiting:
                CurrentPokeState, DelayEnd = ReentryState
            
            # Check for transition to new substate
            elif (MasterTime > DelayEnd): # Time for a state transition!
                if CurrentPokeState == PokeSubstates.BetweenDispensingDelay:
                    ToneStim.Play()
                    DelayEnd = MasterTime + PreDispenseToneDelay
                    CurrentPokeState = PokeSubstates.PreDispenseToneDelay
                elif CurrentPokeState == PokeSubstates.PreDispenseToneDelay:
                    if IsLeftWellPoked:
                        print("sending byte", Well.LeftDispenseMask)
                        Interface.send_byte(Well.LeftDispenseMask)
                    elif IsRightWellPoked:
                        print("sending byte", Well.RightDispenseMask)
                        Interface.send_byte(Well.RightDispenseMask)
                    else:
                        raise Exception('Error in dispense state configuration.')
                    DelayEnd = MasterTime + PostDispenseDelay
                    CurrentPokeState = PokeSubstates.PostDispenseDelay
                elif CurrentPokeState == PokeSubstates.PostDispenseDelay:
                    Interface.send_byte(b'\x00') # reset wells
                    DelayEnd = MasterTime + PostDispenseToneDelay
                    CurrentPokeState = PokeSubstates.PostDispenseToneDelay
                elif CurrentPokeState == PokeSubstates.PostDispenseToneDelay:
                    ToneStim.Stop()
                    DelayEnd = MasterTime + tDelay[RewardNumber]
                    RewardNumber += 1
                    CurrentPokeState = PokeSubstates.BetweenDispensingDelay
                else:
                    raise Exception('Error in PokeSubstates state configuration.')
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

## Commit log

2019-01-01 First commit of firmware and EAGLE cad design
    [PiHat.brd, PiHat.sch]
2019-01-02 Final design for manufacturing
    [PiHat.brd, PiHat.sch]
2019-01-03 Added 3D design files directory and first end caps for PVC axels
    [PVC-AxelMount.SLDPRT, PVC-AxelMount.STL]
2019-01-04 Updated directory names and added EAGLE Cad gitignore
    [PiHat.brd, PiHat.sch]
2019-01-11 Added more treadmill parts
    [BearingMount-80-20.SLDPRT, BearingMount-80-20.STL]
2019-01-17 Updated board after debugging first revision
    [PiHat.brd, PiHat.sch]
2019-01-17 Updated firmware to match PCB
2019-01-22 Added 3D printed standoffs for Pi Hat PCB
    [RaspberryPi Standoff Post v2.SLDPRT, RaspberryPi Standoff Post v2.STL, RaspberryPi Standoff Post.SLDPRT, RaspberryPi Standoff Post.STL]
2019-01-25 Added T Slot Joiner piece
    [TSlotJoiner.SLDPRT, TSlotJoiner.STL]
2019-03-01 Updated height
    [BearingMount-80-20.SLDPRT, BearingMount-80-20.STL]
2019-03-22 Added 80-20 sliding bearing mounts for waterjet cutting
    [BearingMountSlider.DXF, BearingMountSlider.SLDPRT, BearingMountWithoutSlider.DXF, BearingMountWithoutSlider.SLDPRT]
2019-03-26 Updated code some more trying to get 2kHz clock to work
    [PiHat.brd, PiHat.sch]
2019-03-30 Fixed errors and added a FT230 USB/UART Interface to PCB
    [PiHat.brd, PiHat.sch]
2019-03-30 Updated design files
    [BearingMountWithoutSliderTightFit.SLDPRT, BearingSliderTightFit.SLDPRT, Frame_for 2P - Cleaned - Old.SLDPRT, Frame_for 2P - Cleaned.SLDPRT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]
2019-03-30 Updated interface PCB to have proper silkscreen and added manufacturing files
    [PiHat.brd, PiHat.sch]
2019-04-17 Updated firmware code to properly use 2kHz source for newest PCBs. Fixed bug in UART initialization that overwrote P1SEL!
2019-04-19 Updated firmware to make time ISRs use assembly.
2019-04-22 Created entire Quadrature ISR in assembly. Also changed encoder counter to 16 bit
2019-04-23 Split quadrature decoding isr code into it's own files; rewrote UART word-send in assembly; Updated Python test reader for FTDI interfaec
2019-04-23 Added OMAX illustrator files for treadmill arms and 3D printed adaptors for axel and Encoder mount
    [AxelAdaptor.SLDPRT, AxelAdaptor.STL, SliderEncoderMount.SLDPRT, SliderEncoderMount.STL]
2019-04-29 Updated mounting hole positions on encoder mount
    [SliderEncoderMount.SLDPRT, SliderEncoderMount.STL]
2019-04-29 Updated designs for lighter weight acrylic axels
    [AxelAdaptor1375.SLDPRT, AxelAdaptor1375.STL, AxelSpacer_2310.SLDPRT, AxelSpacer_2310.STL]
2019-05-23 Fixed two bugs in design where there were vias that were shorting
    [PiHat.brd]
2019-05-25 Added notes for Raspberry Pi and Python latency test code
2019-05-25 Added more notes for Raspberry Pi
2019-05-25 Added more notes about the Raspberry Pi interface
2019-06-07 Added instructions for getting the Raspberry Pi up and running first.
2019-06-10 Added raspberry pi closed loop testing script
2019-06-22 Added more files for treadmill and wheel mounting
    [3 inch spacer.SLDPRT, 3 inch spacer.STL, BearingAdaptor-SensorMount-PostMount-Centered.SLDPRT, BearingAdaptor-SensorMount-PostMount-Centered.STL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]
2019-06-22 Added datasheet for AMT10 rotational sensor from CUI
2019-06-25 Removed debugging hint which started Unwrapped phase at 100000. Note that we still have PULL DOWN resistors enabled.
2019-06-25 Removed PULL UP resistors.
2019-06-26 Improved tracking of index pin
2019-07-03 added white noise filter for pink noise
2019-07-03 Created a prototype linear track script.
2019-07-03 Raspberry Pi-related updates to Linear Track code
2019-07-06 Double checked and cleaned up headpost designs
    [Frame.SLDPRT, Frame.STL, Frame_for 2P - Cleaned - Old.SLDPRT, HeadPlateHolder-Linear-5_5mm.DXF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]
2019-07-11 moved raspberry pi setup to separate folder
2019-07-20 Updated organization of 3D printed wheel and treadmill parts
    [BearingAdaptor-SensorMount-PostMount-Centered.SLDPRT, BearingAdaptor-SensorMount-PostMount-Centered.STL, BearingAdaptor-SensorMount-PostMount.SLDPRT, BearingAd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]
2019-07-20 Added positioner posts to treadmill side pieces
    [BearingMount - Right.SLDPRT, BearingMount - Right.STL, BearingMount.SLDPRT, BearingMount.STL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]
2019-07-20 More cleanups of 3D printed parts
    [AxelAdaptor.SLDPRT, AxelAdaptor.STL, AxelAdaptor1375.SLDPRT, AxelAdaptor1375.STL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]
2019-07-20 Updated Headplate files (should double check this)
    [HeadPlateHolder.SLDPRT, HeadPlateHolder.dxf, Headplate.dxf]
2019-07-29 Added treadmill belt wheel design and old paper about crowning
    [Pulley_3_5in_Full_bearing.SLDPRT, Pulley_3_5in_Full_bearing.STL]
2019-07-29 Added laser cut acrylc versions of treadmill parts
    [Axel Mount Long.SLDPRT, Axel Mount Long.dxf, Bearing Holder.SLDPRT, Bearing Holder.dxf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]
2019-08-18 Added new Teensy-based hardware breakout board
    [Teensy.brd, Teensy.sch]
2019-09-03 clarified camera output vs. video codec
2019-09-04 clarified video format vs codec for camera setting
2019-09-05 Added a Teensy version of the Firmware.
2019-09-06 re-configured sound and pump logic
2019-12-05 First commit of new auditory VR framework. No sound yet, but created simulator and visualization
2019-12-15 Added treadmill belt wheel designs for 3D extrusion printing
    [Pulley_3_5in_EndCap-Axel.SLDPRT, Pulley_3_5in_EndCap-Axel.STL, Pulley_3_5in_EndCap-Bearing.SLDPRT, Pulley_3_5in_EndCap-Bearing.STL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]
2019-12-16 Added Kinemouse wheel files
    [Circle.SLDPRT, Circle.STL, Circle.dxf, Spokes.SLDPRT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]
2020-01-11 Lots of 3D design changes
    [3DPrintedWheel.SLDPRT, 8600N300_LOW-PROFILE MOUNTED BALL BRNG W ALUM HOUSING.SLDPRT, Bearing Post Assembly.SLDASM, Frame_for 2P - Cleaned - Old.SLDPRT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]
2020-02-25 serial and camera interfaces
2020-03-18 Added a new head plate holder design with two pieces that reach from behind as well as a visualization of the whole assembly. Updated holders so there are standard and 4.72 mm versions (compatible wi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
    [20 in monitor.SLDPRT, BearingAdaptor-SensorMount-PostMount-Centered.SLDPRT, Controller Board Holder.SLDPRT, Head Fixed Assembly 20in.SLDASM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]
2020-08-27 Updated LED holder so that fatter hdmi or usb cables fit
    [Single 8 in Screen and Controller Board Holder.SLDPRT, Single 8 in Screen and Controller Board Holder.STL]

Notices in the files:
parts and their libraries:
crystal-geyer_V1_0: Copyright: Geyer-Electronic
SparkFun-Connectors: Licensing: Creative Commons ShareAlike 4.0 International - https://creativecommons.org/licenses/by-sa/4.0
